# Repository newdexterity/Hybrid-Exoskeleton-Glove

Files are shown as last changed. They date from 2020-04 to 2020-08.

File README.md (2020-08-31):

# Hybrid-Exoskeleton-Glove

**Title:** An Open-Source, Hybrid Exoskeleton Glove Equipped with Variable Stiffness Joints, Abduction Capabilities, and a Telescopic Extra Thumb

**Description:** 
<p align="justify"> Robotic hand exoskeletons have become a popular and efficient technological solution for assisting people that suffer from neurological conditions and for enhancing the capabilities of healthy individuals. This class of devices ranges from rigid and complex structures to soft, lightweight, wearable gloves. Despite the progress in the field, most existing devices do not provide the same dexterity as the healthy human hand. In this work, we propose a hybrid (tendon-driven and pneumatic), lightweight, affordable, easy-to-operate exoskeleton glove equipped with variable stiffness, laminar jamming structures, abduction/adduction capabilities, and a pneumatic telescopic extra thumb that increases grasp stability. </p>  

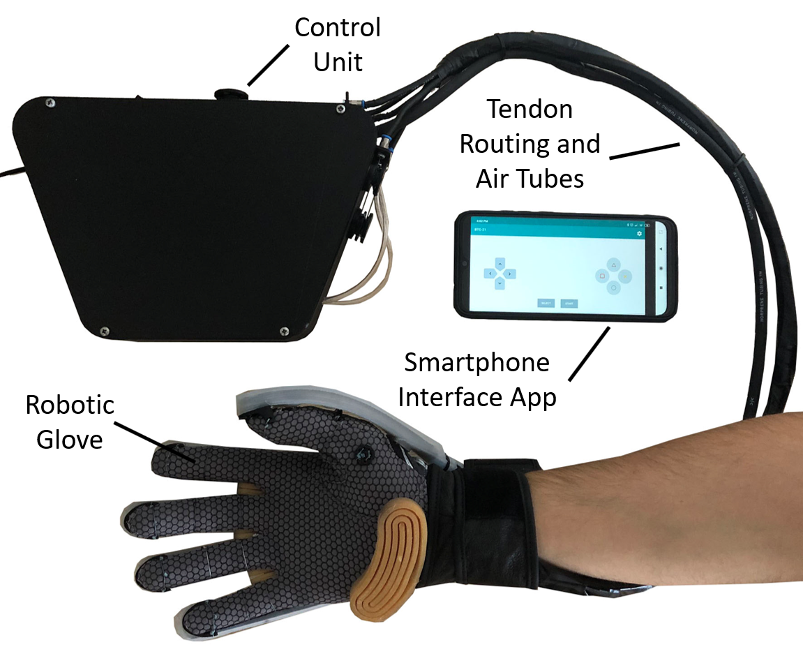
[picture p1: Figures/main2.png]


<p align="justify"> The soft, robotic exoskeleton glove was designed to assist human hands with limited mobility during the motion rehabilitation process and to improve the grasping and dexterous manipulation capabilities of the hand, in both impaired and able-bodied individuals. The proposed device is composed of two main systems: the soft exoskeleton glove and the control unit. The control unit is composed of five Dynamixel XM430-W350-T motors, two mini 12V air pumps, one 12V vacuum pump, three solenoid valves, a microcontroller (Robotis OpenCM9.04), and a small circuit to control the air pumps. All six tendons are connected to the pulleys of the motors and run though polyurethane tubes that are used for tendon routing from the control unit to the soft glove. The ring and pinky fingers have a supplementary role during object grasping \cite{liarokapis2013quantifying}, therefore, they are connected to the same motor. A vacuum tube connects the vacuum pump to the jamming structures located at the back of the hand, and another two tubes connect the air pumps to the abduction soft actuators and the inflatable, telescopic thumb.  </p> 

<p align="justify"> The soft glove system of the proposed device is composed of a thin, high sensibility glove, a tendon-driven system that consists of six artificial tendons, a pneumatic system that consists of four soft actuators, and five laminar jamming structures. Five plastic tendon termination structures are stitched onto the fingertips of the glove. Soft anchor points have been added in the glove structure for rerouting the tendon, offering better sensibility of the grasped objects than the rigid anchor points. The tendon-driven system has a tendon connected to each of the fingertip structures and an extra tendon that is connected to the thumb's interphalangeal joint region so as to allow for the execution of the thumb's opposition motion. A tendon-driven solution for the thumb abduction / opposition was chosen over a soft actuator based solution, in order to avoid the obstruction of the region between the index and the thumb, as many different grasps types require the object to be positioned in-between the thumb and the index metacarpophalangeal joints (in the human hand purlicue area). The tendons used in the exoskeleton glove are made out of a low friction braided fiber of high-performance UHMWPE (Ultra-High Molecular Weight Polyethylene) and can withstand forces up to 500 N. The soft actuators are used for two different purposes, to allow for the execution of the abduction / adduction motion of the fingers and to increase grasp stability by activating a telescopic extra thumb that provides grasp support. Three pneumatic chambers have been developed with a "V" shape, and they have been fixed in the region in between the fingers to facilitate the execution of the abduction motion of the fingers. The soft actuator was designed to provide active assistance on finger abduction and passive on finger adduction, once the human hand is naturally adducted.  </p> 

<p align="justify"> The soft actuators that have been designed are described in the following subsections. At the back of each digit, laminar jamming structures are attached to control the force required to close the digits, to maintain the fingers steady in a desired configuration, and to perform passive extension of the fingers keeping the hand in its natural, zero effort position. The laminar jamming structures can achieve multiple stiffnesses by applying a pressure gradient into the system and relying on the friction between the layers. A single vacuum pump is used to jam the layers of all fingers, enabling variable joint stiffness. A flex sensor was placed at the index finger region and is used to trigger a desired function of the exoskeleton glove when a set bending angle is achieved.  </p> 

<p align="justify"> The operation of the device is straightforward. Using the smartphone app, the user selects the mode desired to control the exoskeleton glove. The user can combine the motions (e.g., full grasp with abducted fingers or tripod grasp with the extra thumb inflated and the jamming structures activated). The flex sensor can be selected to trigger the desired motion when a set bending angle is reached. The information is transmitted to a microcontroller through Bluetooth communication. Then, the microcontroller activates the chosen actuators that are connected to the glove. Each air supply is connected to a solenoid valve that is used to release the air pressure of the system when the glove returns to its original position. The entire system is powered by a 12V power supply. A battery can be added to the control unit to make the device portable and wearable. The amount of force applied by each finger is determined through a current control of each motor and can be adjusted according to the user's needs. </p>  

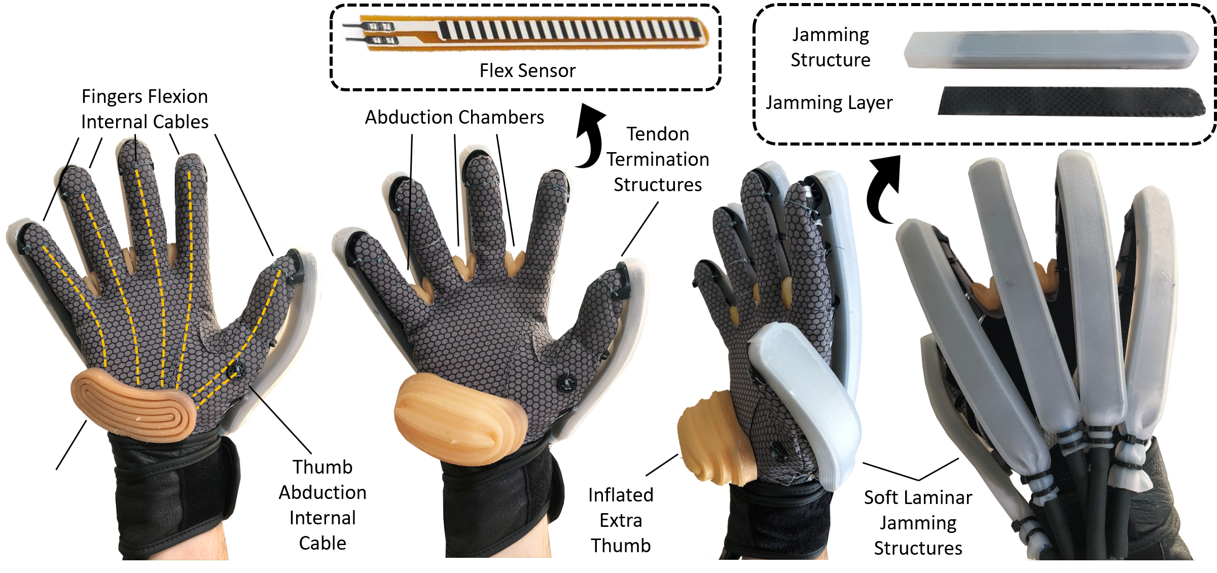
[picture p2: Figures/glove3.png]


<p align="justify"> The project is distributed under the Creative Commons Attribution 4.0 International License (https://creativecommons.org/licenses/by/4.0/) </p>

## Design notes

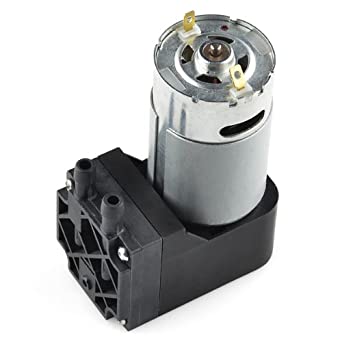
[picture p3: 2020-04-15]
Electronics and Actuators/12V_Vacuum_Pump.jpg

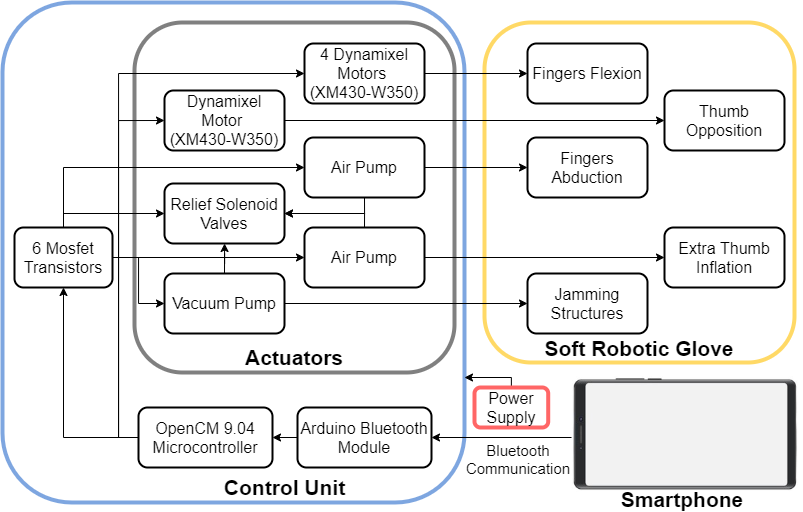
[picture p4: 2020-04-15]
Electronics and Actuators/Electronics_Diagram.png

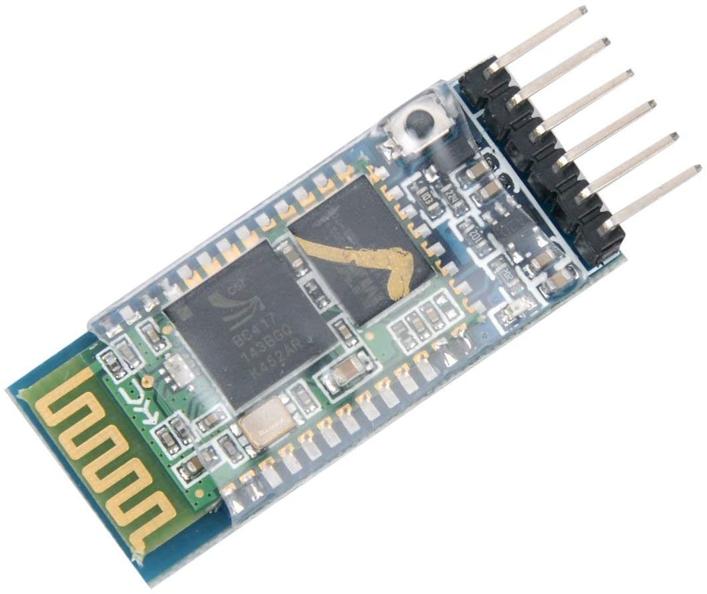
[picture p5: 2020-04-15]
Electronics and Actuators/Bluetooth_Module.jpeg

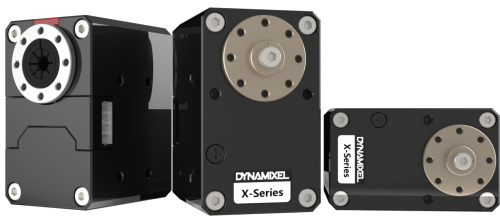
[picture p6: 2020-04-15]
Electronics and Actuators/Dynamixel_Motor.png

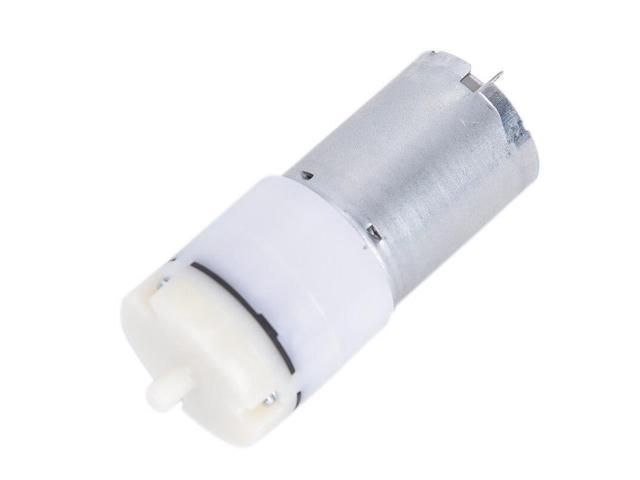
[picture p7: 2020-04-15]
Electronics and Actuators/12V_Air_Pump.jpg

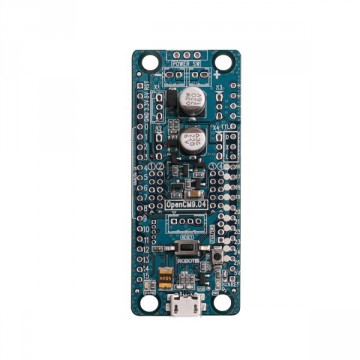
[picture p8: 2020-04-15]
Electronics and Actuators/OpenCM.jpg

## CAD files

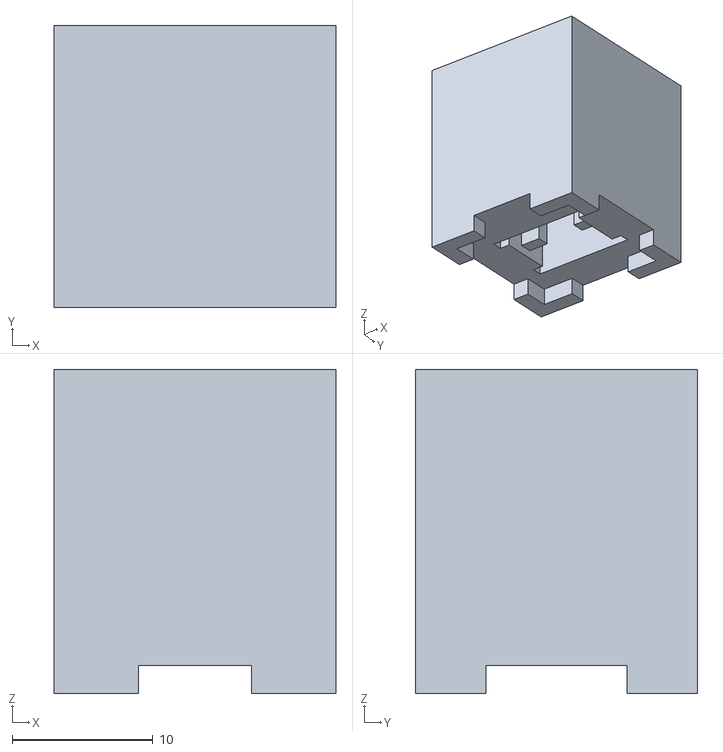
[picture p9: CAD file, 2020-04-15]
CAD/Abduction Chambers/Abduction_Chamber_Base_Mold.STL
20.0 x 20.0 x 23.0

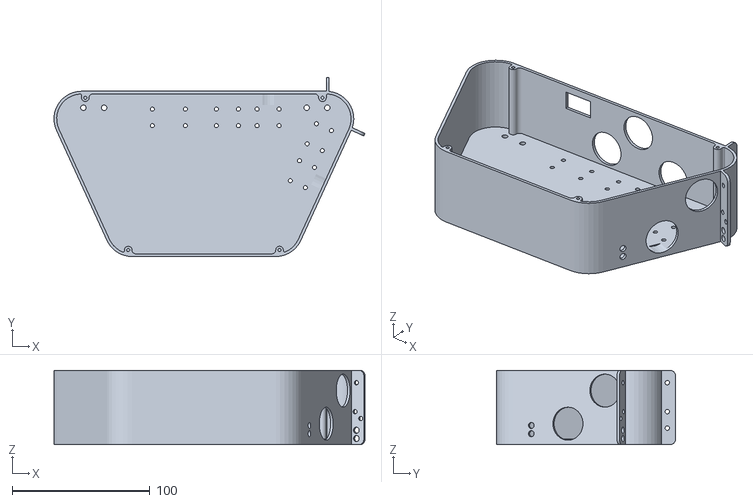
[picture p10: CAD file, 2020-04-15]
CAD/Control Unit/Control_Unit_Box.STL
225.7 x 130.0 x 54.0

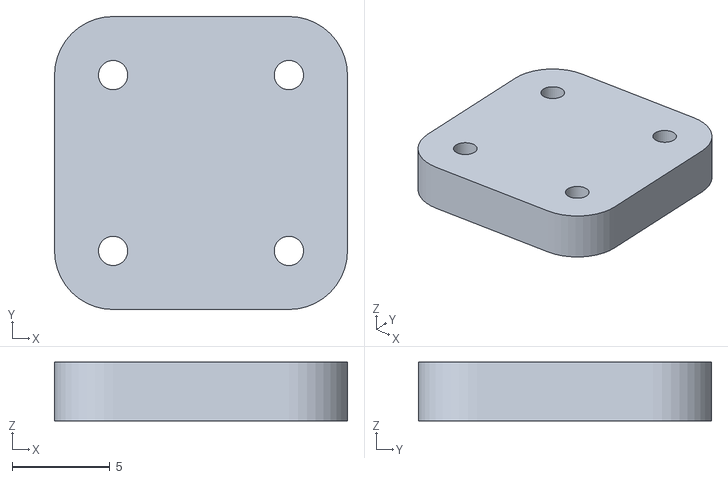
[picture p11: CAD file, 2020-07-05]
CAD/Jamming Structures/pouch_glove_connection.STL
15.0 x 15.0 x 3.00

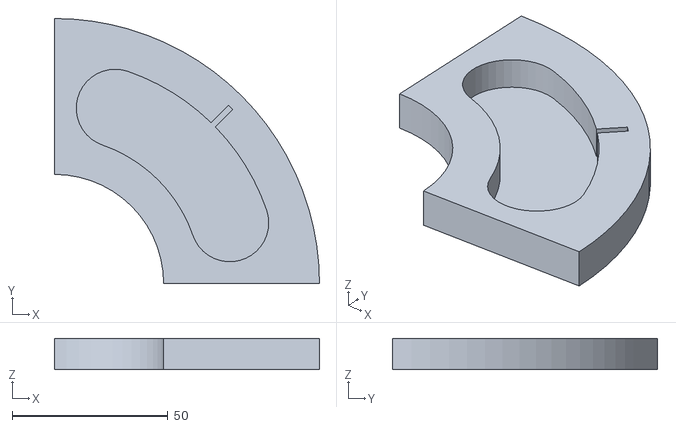
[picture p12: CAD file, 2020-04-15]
CAD/Telescopic Extra Thumb/Telescopic_Thumb_Base_Layer_Step2.STL
85.0 x 85.0 x 10.0

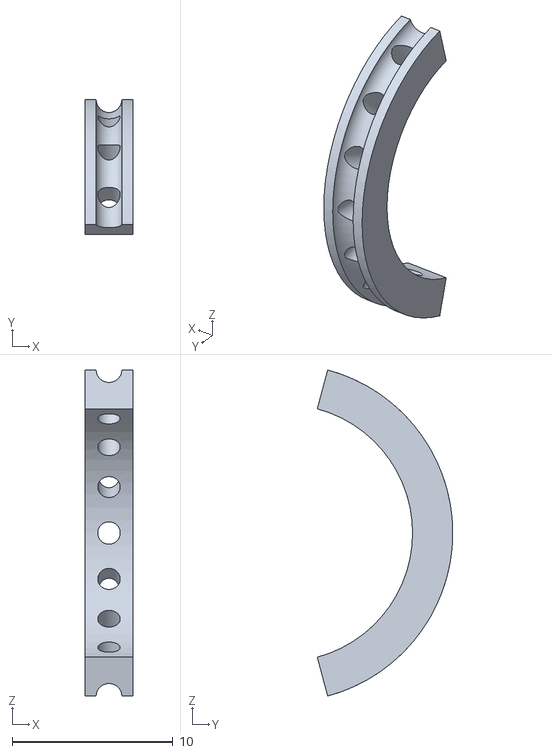
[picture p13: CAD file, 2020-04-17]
CAD/Tendon Routing System/Anchor_top.STL
3.00 x 8.43 x 20.3

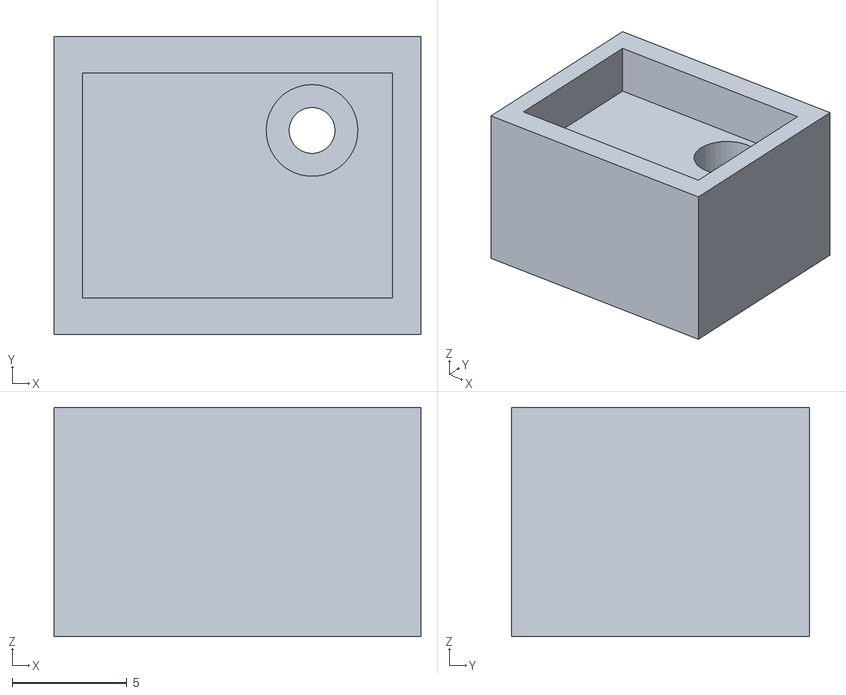
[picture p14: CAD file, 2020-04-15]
CAD/Abduction Chambers/Abduction_Chamber_Outer_Mold.STL
16.0 x 13.0 x 10.0

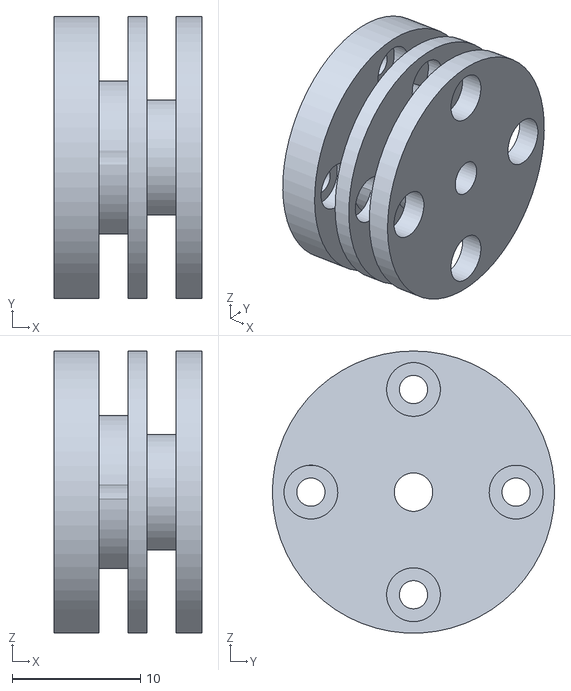
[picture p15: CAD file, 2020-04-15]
CAD/Control Unit/Pulley_2_Channels.STL
11.5 x 22.0 x 22.0

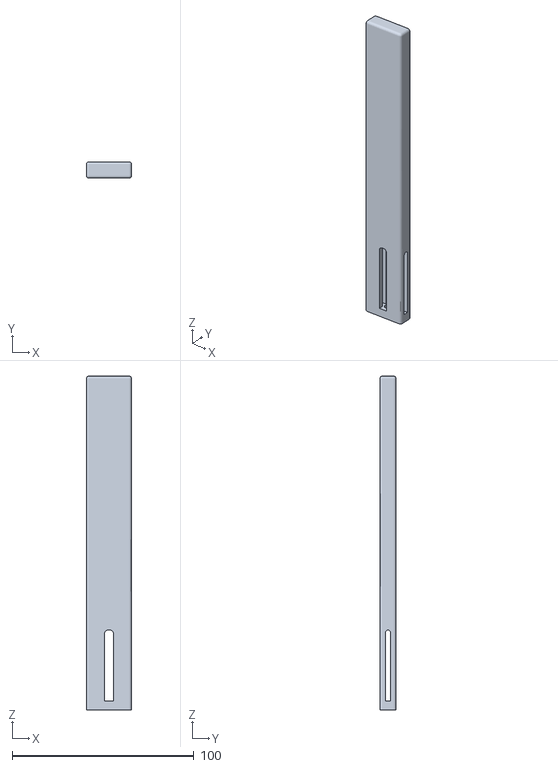
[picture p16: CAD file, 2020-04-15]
CAD/Jamming Structures/Pouch_Center_Mold.STL
25.0 x 9.00 x 184.0

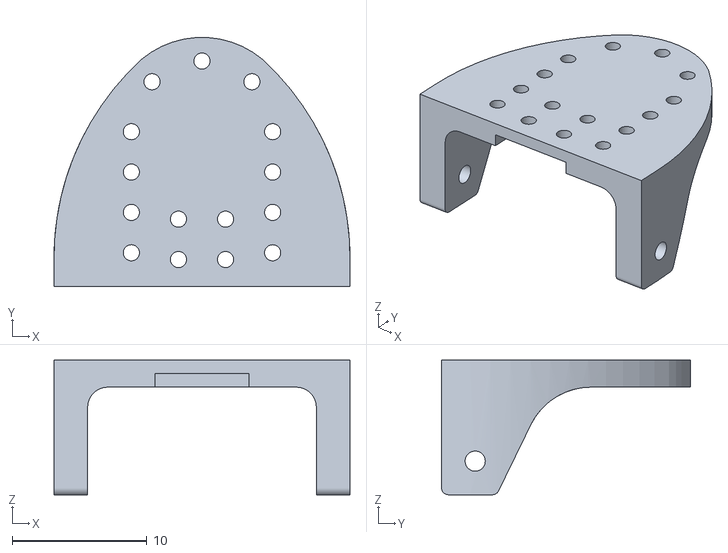
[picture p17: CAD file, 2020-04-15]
CAD/Tendon Routing System/Nail_glove.STL
22.0 x 18.5 x 10.0

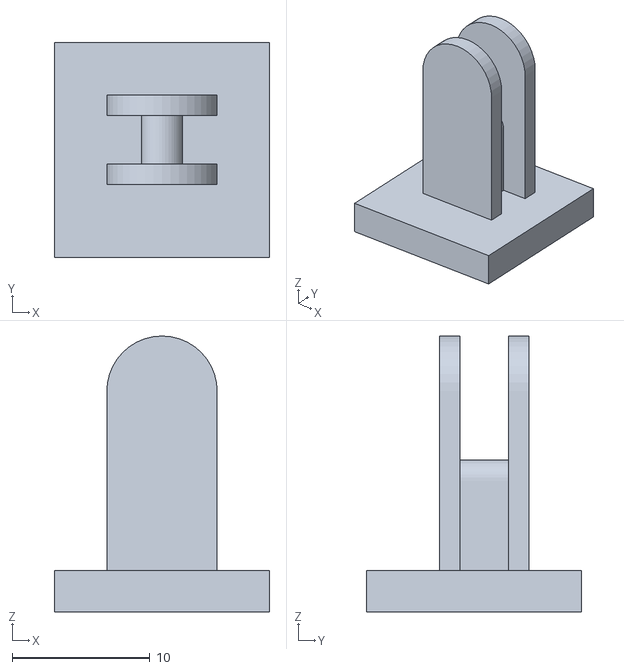
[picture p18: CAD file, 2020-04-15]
CAD/Abduction Chambers/Abduction_Chamber_Inner_Mold.STL
15.6 x 15.6 x 20.0

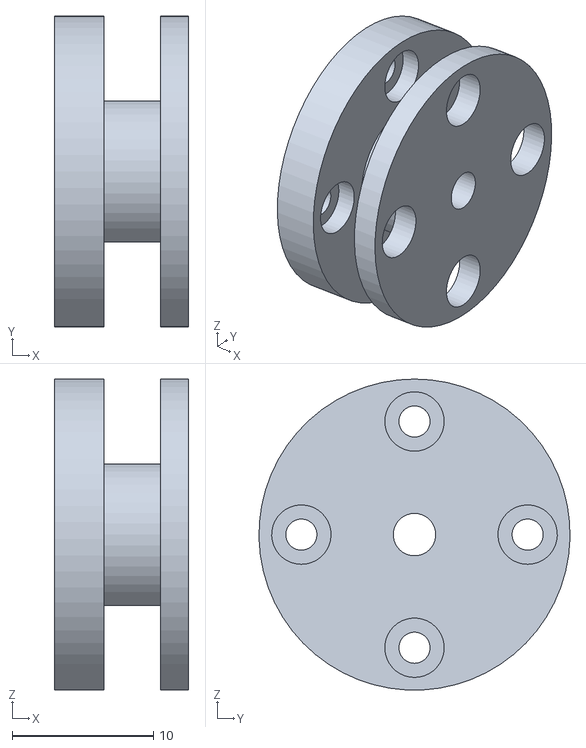
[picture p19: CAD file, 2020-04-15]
CAD/Control Unit/Pulley.STL
9.50 x 22.0 x 22.0

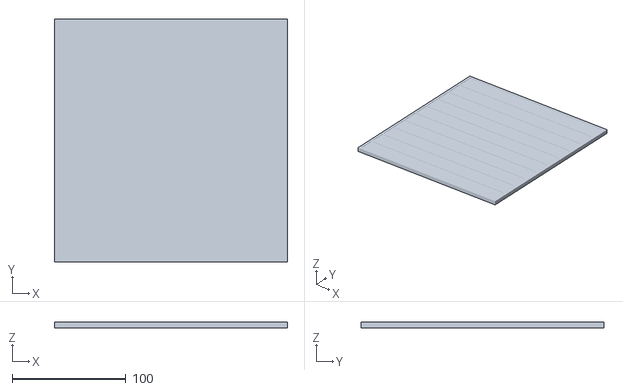
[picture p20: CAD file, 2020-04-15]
CAD/Jamming Structures/Layer_Mold_Base.STL
205.0 x 214.0 x 5.00

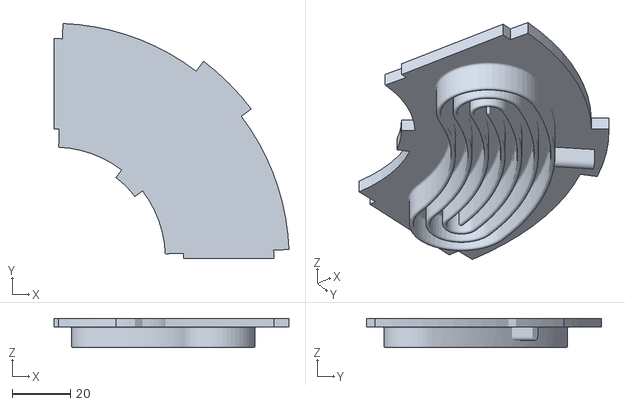
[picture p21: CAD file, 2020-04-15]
CAD/Telescopic Extra Thumb/Telescopic_Thumb_Top_Step1.STL
80.7 x 80.7 x 10.0

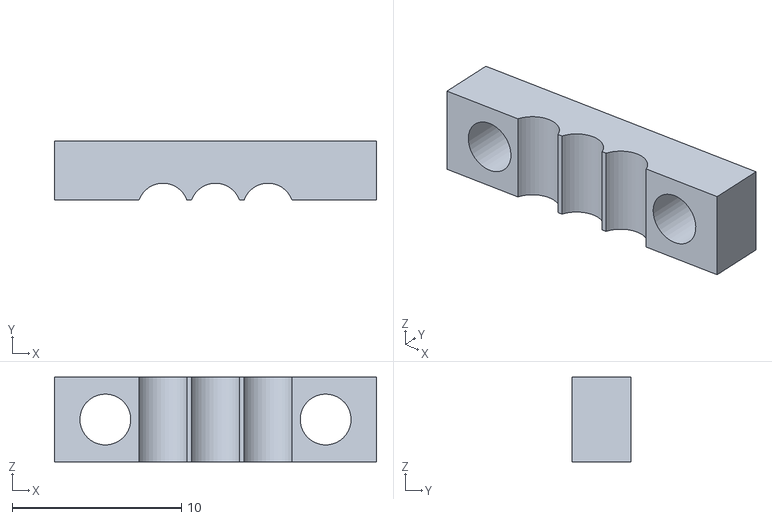
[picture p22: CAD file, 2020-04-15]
CAD/Tendon Routing System/Glove_holder.STL
19.0 x 3.50 x 5.00

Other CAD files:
CAD/Telescopic Extra Thumb/Telescopic_Thumb_Bond_Step3.STL
CAD/Control Unit/Control_Unit_Lid.STL
CAD/Jamming Structures/Pouch_Outer_Mold.STL
CAD/Telescopic Extra Thumb/Telescopic_Thumb_Base_Step1.STL
CAD/Jamming Structures/Layer_Mold_Top.STL

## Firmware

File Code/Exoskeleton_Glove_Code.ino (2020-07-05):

/*******************************************************************************
* Copyright 2016 ROBOTIS CO., LTD.
*
* Licensed under the Apache License, Version 2.0 (the "License");
* you may not use this file except in compliance with the License.
* You may obtain a copy of the License at
*
*     http://www.apache.org/licenses/LICENSE-2.0
*
* Unless required by applicable law or agreed to in writing, software
* distributed under the License is distributed on an "AS IS" BASIS,
* WITHOUT WARRANTIES OR CONDITIONS OF ANY KIND, either express or implied.
* See the License for the specific language governing permissions and
* limitations under the License.
*******************************************************************************/

/* Authors: Taehun Lim (Darby) */

#include <DynamixelWorkbench.h>

#if defined(__OPENCM904__)
  #define DEVICE_NAME "1" //Dynamixel on Serial3(USART3)  <-OpenCM 485EXP
#elif defined(__OPENCR__)
  #define DEVICE_NAME ""
#endif   

#define BAUDRATE  1000000
#define DXL_ID    1
#define ledPin 16
int state = 0;
int motorpos=0;
int jamming = 10;
int chamber = 11;
int abduction = 12;
int solenoidjamming = 13;
int solenoidchamber = 14;
int solenoidabduction = 15;


DynamixelWorkbench dxl_wb;

void setup() 
{
  Serial.begin(115200);
  Serial2.begin(115200);
  //while(!Serial); // Wait for Opening Serial Monitor
  pinMode(ledPin, OUTPUT);
  digitalWrite(ledPin, LOW);
  pinMode(chamber, OUTPUT);
  pinMode(abduction, OUTPUT);
  pinMode(jamming, OUTPUT);
  pinMode(solenoidchamber, OUTPUT);
  pinMode(solenoidabduction, OUTPUT);
  pinMode(solenoidjamming, OUTPUT);
  const char *log;
  bool result = false;
  bool result2 = false;
  bool result3 = false;
  bool result4 = false;
  bool result5 = false;
  
  // Change the motor ID and set the baud rate using the Robotis R+ Manager 2.0 
  uint8_t dxl_id = DXL_ID;
  uint8_t dx2_id = 2;
  uint8_t dx3_id = 3;
  uint8_t dx4_id = 4;
  uint8_t dx5_id = 5;
  
  uint16_t model_number = 0;
  // This initialization tests all motors and make sure all motors have the correct ID and are properly set up. 

  result = dxl_wb.init(DEVICE_NAME, BAUDRATE, &log);
  if (result == false)
  {
    Serial.println(log);
    Serial.println("Failed to init");
  }
  else
  {
    Serial.print("Succeeded to init : ");
    Serial.println(BAUDRATE);  
  }

  result = dxl_wb.ping(dxl_id, &model_number, &log);
  result2 = dxl_wb.ping(dx2_id, &model_number, &log);
  result3 = dxl_wb.ping(dx3_id, &model_number, &log);
  result4 = dxl_wb.ping(dx4_id, &model_number, &log);
  result5 = dxl_wb.ping(dx5_id, &model_number, &log);
  if (result == false && result2 == false && result3 == false && result4 == false && result5 == false)
  {
    Serial.println(log);
    Serial.println("Failed to ping");
  }
  else
  {
    Serial.println("Succeeded to ping");
    Serial.print("id : ");
    Serial.print(dxl_id);
    Serial.print(" model_number : ");
    Serial.println(model_number);
  }

  result = dxl_wb.currentBasedPositionMode(dxl_id, 30, &log);
  result2 = dxl_wb.currentBasedPositionMode(dx2_id, 150, &log);
  result3 = dxl_wb.currentBasedPositionMode(dx3_id, 30, &log);
  result4 = dxl_wb.currentBasedPositionMode(dx4_id, 30, &log);
  result5 = dxl_wb.currentBasedPositionMode(dx5_id, 30, &log);
  if (result == false && result2 == false && result3 == false && result4 == false && result5 == false)
  {
    Serial.println(log);
    Serial.println("Failed to change current based position mode");
  }
  else
  {
    Serial.println("Succeed to change current based position mode");
    Serial.println("Dynamixel is moving...");

    for (int count = 0; count < 1; count++) //All motors testing and Motor Calibration 
    {
      dxl_wb.goalPosition(dxl_id, (int32_t)0);
      dxl_wb.goalPosition(dx2_id, (int32_t)0);
      dxl_wb.goalPosition(dx3_id, (int32_t)0);
      dxl_wb.goalPosition(dx4_id, (int32_t)0);
      dxl_wb.goalPosition(dx5_id, (int32_t)0);
      delay(1500);

    }
  }
}

void loop() 
{
 if(Serial2.available() > 0){ // Checks whether data is comming from the serial port
    state = Serial2.read(); // Reads the data from the serial port
    Serial.println(state); // Make sure the values received from the bluetooth module are compatible with the code
    state=state-48;
    int flex = 0;
 
 if (state == 1) { //Full Grasp: 5 fingers move
  dxl_wb.goalPosition(1, (int32_t)8000);
  dxl_wb.goalPosition(2, (int32_t)8000);
  dxl_wb.goalPosition(3, (int32_t)8000);
  dxl_wb.goalPosition(4, (int32_t)8000);
  dxl_wb.goalPosition(5, (int32_t)8000);
  delay(1500);
  state = 0;
 }
 else if (state == 2) { // Tripod Grasp: 3 fingers move
  dxl_wb.goalPosition(1, (int32_t)8000);
  dxl_wb.goalPosition(2, (int32_t)8000);
  dxl_wb.goalPosition(3, (int32_t)8000);
  delay(1000);
  state = 0;}  else if (state == 3) { //Pinch Grasp: 2 fingers move

  dxl_wb.goalPosition(2, (int32_t)12000);
  dxl_wb.goalPosition(3, (int32_t)8000);
  dxl_wb.goalPosition(5, (int32_t)8000);
  delay(1000);
  state = 0;} else if (state == 4) { //Abduction Chambers
  delay(500);
  for (int i = 0; i <= 255; i++) {
       analogWrite(abduction, i);
       delay(4);
  } 
  delay(200);
  state = 0;} else if (state == 5) {//Jamming structures
  delay(500);
  for (int i = 0; i <= 255; i++) {
       analogWrite(jamming, i);
       delay(4);
  } 
  delay(200);
  state = 0;} else if (state == 6) {//Chamber
  delay(500);
  for (int i = 0; i <= 255; i++) {
       analogWrite(chamber, i);
       delay(4);
  } 
  delay(200);
  state = 0;} else if (state == 7) {//Return to rest: press the return to rest button to return the motors to the initial position and to release all the solenoid valves
  dxl_wb.goalPosition(1, (int32_t)0);
  dxl_wb.goalPosition(2, (int32_t)0);
  dxl_wb.goalPosition(3, (int32_t)0);
  dxl_wb.goalPosition(4, (int32_t)0);
  dxl_wb.goalPosition(5, (int32_t)0);
  delay(500);
           analogWrite(abduction, 0);
           delay(20);
           analogWrite(jamming, 0);
           delay(20);
           analogWrite(chamber, 0);
           delay(20);
           analogWrite(solenoidabduction, 255);
           delay(20);
           analogWrite(solenoidjamming, 255);
           delay(20);
           analogWrite(solenoidchamber, 255);
           delay(1000);
           analogWrite(solenoidabduction, 0);
           delay(20);
           analogWrite(solenoidjamming, 0);
           delay(20);
           analogWrite(solenoidchamber, 0);
  delay(50);
  state = 0;} else if (state == 8) { //flex sensor
    while (flex<5){
    int sensorValue = analogRead(A0);
    delay(2);
    Serial.println(sensorValue);
    if (sensorValue <=5){
    flex = flex + 1;
    }
    delay(10);
    }
        for (int i = 0; i <= 255; i++) {
       analogWrite(jamming, i);
       delay(4);
        }
  } else if (state == 9) { //Key Grasp

  dxl_wb.goalPosition(2, (int32_t)12000);
  dxl_wb.goalPosition(3, (int32_t)8000);
  delay(1000);}

  else if (state == 10) { //Thumb Abdcution
  dxl_wb.goalPosition(5, (int32_t)8000);
  delay(1000);}

  }
 }
 
